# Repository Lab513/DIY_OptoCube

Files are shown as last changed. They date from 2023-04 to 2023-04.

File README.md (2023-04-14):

# DIY_OptoCube
The OptoCube is a static temperature-controlled incubator equipped with a DMD to project light patterns on a set of agar plates. The agar plates are placed on top of a scanner to record time-lapse images of microbial growth. This setup allows high spatial and temporal resolution of light patterning (~ 0.1 mm, ~ 1 s) compared to the dimensions and dynamics of microbial colonies (> 1 mm, > 1 hour).

## Building your own OptoCube
Building an OptoCube is relatively straightforward. You need to gather a static incubator of relatively large dimension, a Digital micromirror device, a micro controller and a flatbed scanner. We propose here a set of devices that worked for us, but other commercial or DIY alternatives are of course possible.

-	Incubator : Memert (any large enough static incubator will do)
-	DMD : DLP® LightCrafter™ 4500 TI
-	Scanner : Canon LIDE400. Note that, we opened the glass cover and apply black tape on some part of the bottom which are reflecting surfaces (this prevent undesired optogenetic activation reflection artefacts).
-	Microcontroler : Arduino UNO.

Briefly, the DMD was mounted on an incubator rack (OpenBeam construction kits). The scanner was placed below, facing up. The distance between the scanner glass and the DMD lens was 39cm. 

## Controlling the DMD with the Arduino board.
The DMD was powered with a 12V 4.16A power supply and connected to the Arduino at the pins J11.4, J11.5 and J11.6 using a molex 51021-0600 connector. The scanner was connected to the computer with a USB cable. The Arduino UNO was also connected to the computer with a USB cable and was controlling the DMD using its pin number 2 to apply 3.3V at the J11.5 pin trough a voltage divider (2.2kOhm and 3.3kOhm). The Arduino 3.3V pin was connected to the J11.4 pin and the ground pin to the J11.6. 
We use Jupyter to drive the OptoCube. To run the Jupyter script, you need to install the following package: serial (https://pypi.org/project/pyserial/) , time (https://docs.python.org/fr/3/library/time.html) and os.( https://docs.python.org/fr/3/library/os.html). You can alternatively directly download an anaconda environment containing all required packages from our github webpage.
https://anaconda.org/matthias.lebec/optocube

The DLP® LightCrafter™ 4500 TI is a Digital Micromirror Device composed of 912 × 1140 micromirror that can switch ON or OFF to reflect the light coming from integrated LEDs (Red, Green and Blue). The projected pixel intensity is controlled by Pulse Width Modulation. An important technical limitation is that even when the mirrors are completely OFF, there is a significant amount of light leaking out of the DMD onto the projected surface. The DMD offer two main modes of projection: video mode or sequence mode. The video mode is performed trough classical HDMI communication with a computer, allowing for straightforward and dynamic patterning. However, the range of light intensity in video mode is quite reduce, with a strong leaking. We thus used the sequence mode which give better intensities range (from 0.0014 mW.cm-² to 1.13mW/.cm-² for the blue LED). The main drawback of this mode is the lack of flexibility to change the mask being projected by the DMD. The mask must be loaded in the DMD before the experiment started using the DLPLCR software, and the maximum number of 8-bits masks that can be stored was 6. We use the DLPLCR software (“DLPLCR4500EVM-GUI” can be download here https://www.ti.com/tool/DLPLCR4500EVM) to create and load the masks, and to design the pattern sequence. More information on the procedure can be found in the DMD user guide. Briefly the workflow is the following:

1.	Create a 8 bits image in the BMP format, of dimension 912x1140 (Width x Height). The pattern has to be drawn with a 200% deformation in the vertical axis (due to the diamond shaped of the mirrors, see DLPLCR documentation for details)
2.	This image is transformed by the DLPLCR software to a 24 bits BMP image.
3.	In the DLPLCR software we load the 24 bits images to add to the firmware. The firmware is then built.
4.	Connect the computer to the DMD using a USB cable and power the DMD (this is not mandatory for the previous step).
5.	Load the firmware in the DMD.
6.	Edit the pattern sequence and save it in the DMD. You can then unplug the computer to the DMD.

## Seeting up the VueScan software to drive the scanner.
We used the following parameters. Note that the use of this software is not mandatory and other open-source software that can drive a scanner should do the trick. 
-	Media: “Black&White”
-	Media size: A4
-	Output file: 16 bits greyscale .tiff (no reduction nor compression)
-	Make Grey from: Auto
-	Scan resolution: 600 dpi
-	Number of passes: 1
-	Color balance: “None”

## Additional Requirements
The petri dishes lids can generate imaging artefacts due to light reflexion. To prevent this, we used 3D printed parts (“PlateTilterAngle5”) to tilt the lids of the petri dishes at 5°.
3D printed part “PlateTilterAngle5”

Note that to maximize the image acquisition quality you should ensure that agar plates are: 
1.	Highly transparent to avoid light scattering (this is why we relied on Phytagel).
2.	The gel layer is thin to allow the yeast layer to be in the focal plan of the scanner.
3.	The lid should be coated with a surfactant solution to reduce droplet formation due to condensation. We used a solution of Triton 100X 0.05% (v/v) (Eth 20%)

## License

<br />Ce(tte) œuvre est mise à disposition selon les termes de la <a rel="license" href="http://creativecommons.org/licenses/by-nc-sa/4.0/">Licence Creative Commons Attribution - Pas d’Utilisation Commerciale - Partage dans les Mêmes Conditions 4.0 International</a>.

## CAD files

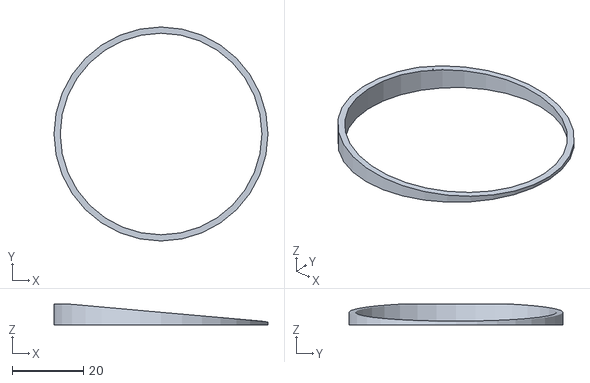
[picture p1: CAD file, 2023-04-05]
PlateTilterAngle5.stl
60.0 x 60.0 x 5.84
